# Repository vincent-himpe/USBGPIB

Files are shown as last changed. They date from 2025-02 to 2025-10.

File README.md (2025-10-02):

USBGPIB
=======

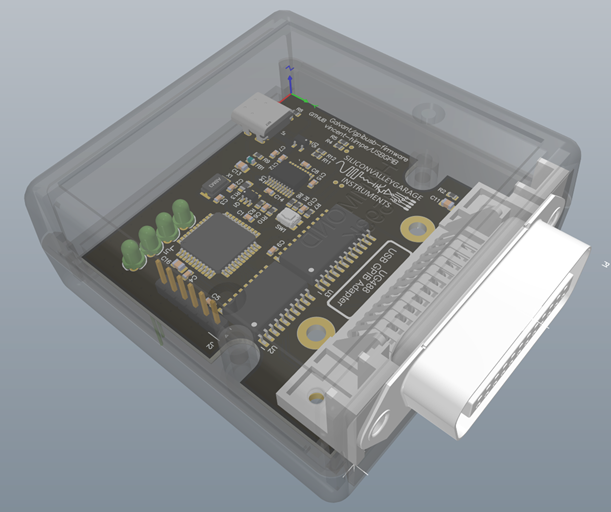
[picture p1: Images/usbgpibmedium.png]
mk-iii


This is a fork of the USB to GPIB adapter found at https://github.com/Galvant/gpibusb-pcb

See the following repos for more information

Firmware: https://www.github.com/Galvant/gpibusb-firmware

Docs: https://www.github.com/Galvant/gpibusb-documentation

Bootloader: https://www.github.com/Galvant/gpibusb-bootloader

This is only a HARDWARE fork ! The existing firmware/bootloadr/documentation will work on this board.

The original data is preserved in the REV4 folder.

## Changes

- Converted project to Altium Designer
- Changed the FTDI chip from a QFN package to SSO20 for easier soldering.
- Clean up schematic.
- Clean up all footprints and load 3D models
- Change board outline.
- Redone all routing.
- Change to 4 layer board.
- Designed the board to fit a small off-the-shelf Hammond enclosure.
- Endcap available as a PCB so you don;t have to drill the plastic endcap of the box.
- USB-C connector

## Layout

The Board is a 4 layer PCB that can easily be produced by the likes of JLCPCB or PCBway.  A full production pack (Gerber / NCdrill, BOM , Pick and place ) is available. 

## Assembly

The Bom and pick and place is included for assembly.

## Source Files

All source files are available in Altium Format. That's what i know, have and use. Other CAD programs most likely can import those. So you can modify.

## License

This work is released under the Creative Commons Attribution-Sharealike 3.0 license.
See http://creativecommons.org/licenses/by-sa/3.0/ or the included license/LICENSE.TXT file for more information.

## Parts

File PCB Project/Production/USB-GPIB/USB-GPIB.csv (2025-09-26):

Description | Designator | Quantity | LCSC
CAPACITOR,CERAMIC,100nF,50V,X7R,0603 | C1, C4, C5, C6, C7, C8, C9, C10, C12, C14, C15 | 11 | C127833
CAPACITOR,CERAMIC,18pF,50V,C0G,0603 | C2, C3 | 2 | C2169518
CAPACITOR,CERAMIC,10nF,200V,X7R,0805,ESD | C11 | 1 | C36911368
CAPACITOR,CERAMIC,10uF,25V,X5R,0805 | C13, C16 | 2 | C3039694
LED,TH,GREEN,42mCd,3MM, CONN,GPIB,24P,RIGHT ANGLE,TH | D1, D2, D3, D4, P1 | 5
DIODE,TVS,DUAL,UNIDIRECTIONAL,USB | D5 | 1 | C22358704
FERRITE,1KZ@100MHz,0R2DC,0603 | FB1 | 1 | C160982
OSHW LOGO, [NoValue] | G***, J2 | 2
CONN,USB-C,16P,RA,TH,8.94X9.17 | J1 | 1 | C7095263
XSTR,PMOS,20V,5.97A,VISHAY,SI3443,SOT26 | Q1 | 1 | C727385
RESISTOR,10K,1%,100mW,0603 (1608) | R1, R3 | 2 | C98220
RESISTOR,4K7,1%,100mW,0603 (1608) | R2 | 1 | C99782
RESISTOR,1K,1%,100mW,0603 (1608) | R4, R5, R6, R7, R10 | 5 | C22548
RESISTOR,5K1,1%,100mW,0603 (1608) | R8, R9 | 2 | C105580
RESISTOR,27R,1%,100mW,0603 (1608) | R11, R12 | 2 | C137753
RESISTOR,0R,JUMPER | R13 | 1 | C96345
SW,SMD,TACT,4PIN,2.9X3.5,4PIN | SW1 | 1 | C483888
IC,CPU,MICROCHIP,PIC18F4520,TQFP44 | U1 | 1 | C9734
IC,XCVR,GPIB,DATA.TI,SN75160DW,SO20W | U2 | 1 | C882412
IC,XCVR,GPIB,CONTROL,TI,SN75162DW,SO24W | U3 | 1 | C2863933
IC,XCVR,USB UART,FTDI,FT231XS-R,TSSOP20 | U4 | 1 | C132160
XTAL,18.432MHz,ABRACON ABM3,SMD5032 | X1 | 1 | C1985331

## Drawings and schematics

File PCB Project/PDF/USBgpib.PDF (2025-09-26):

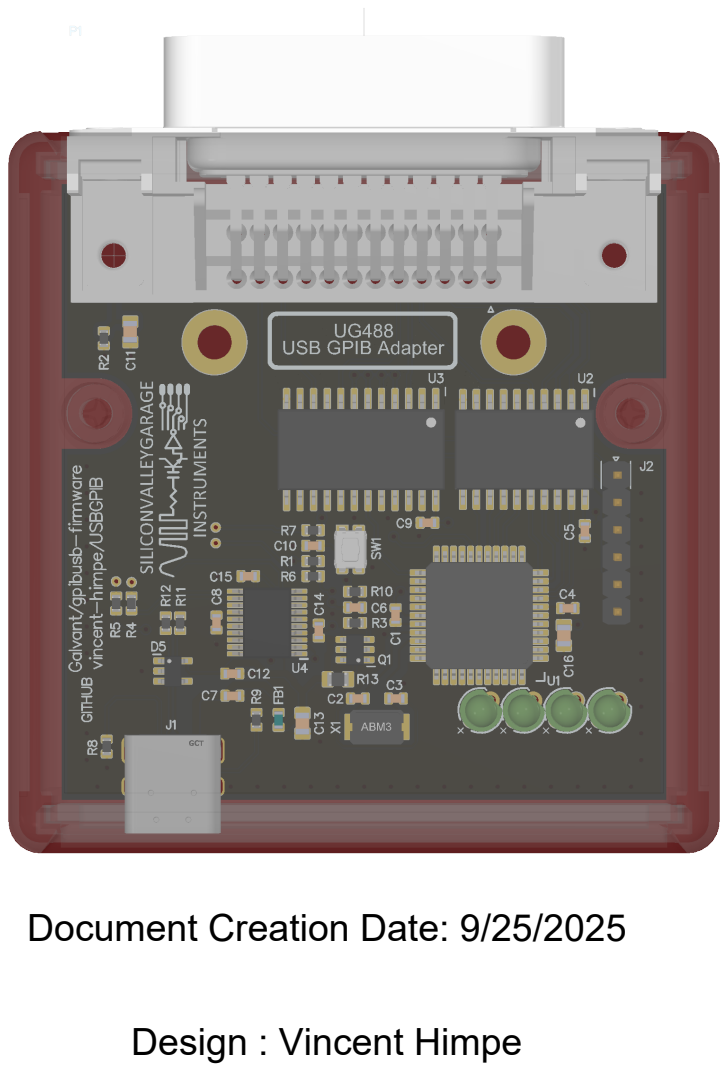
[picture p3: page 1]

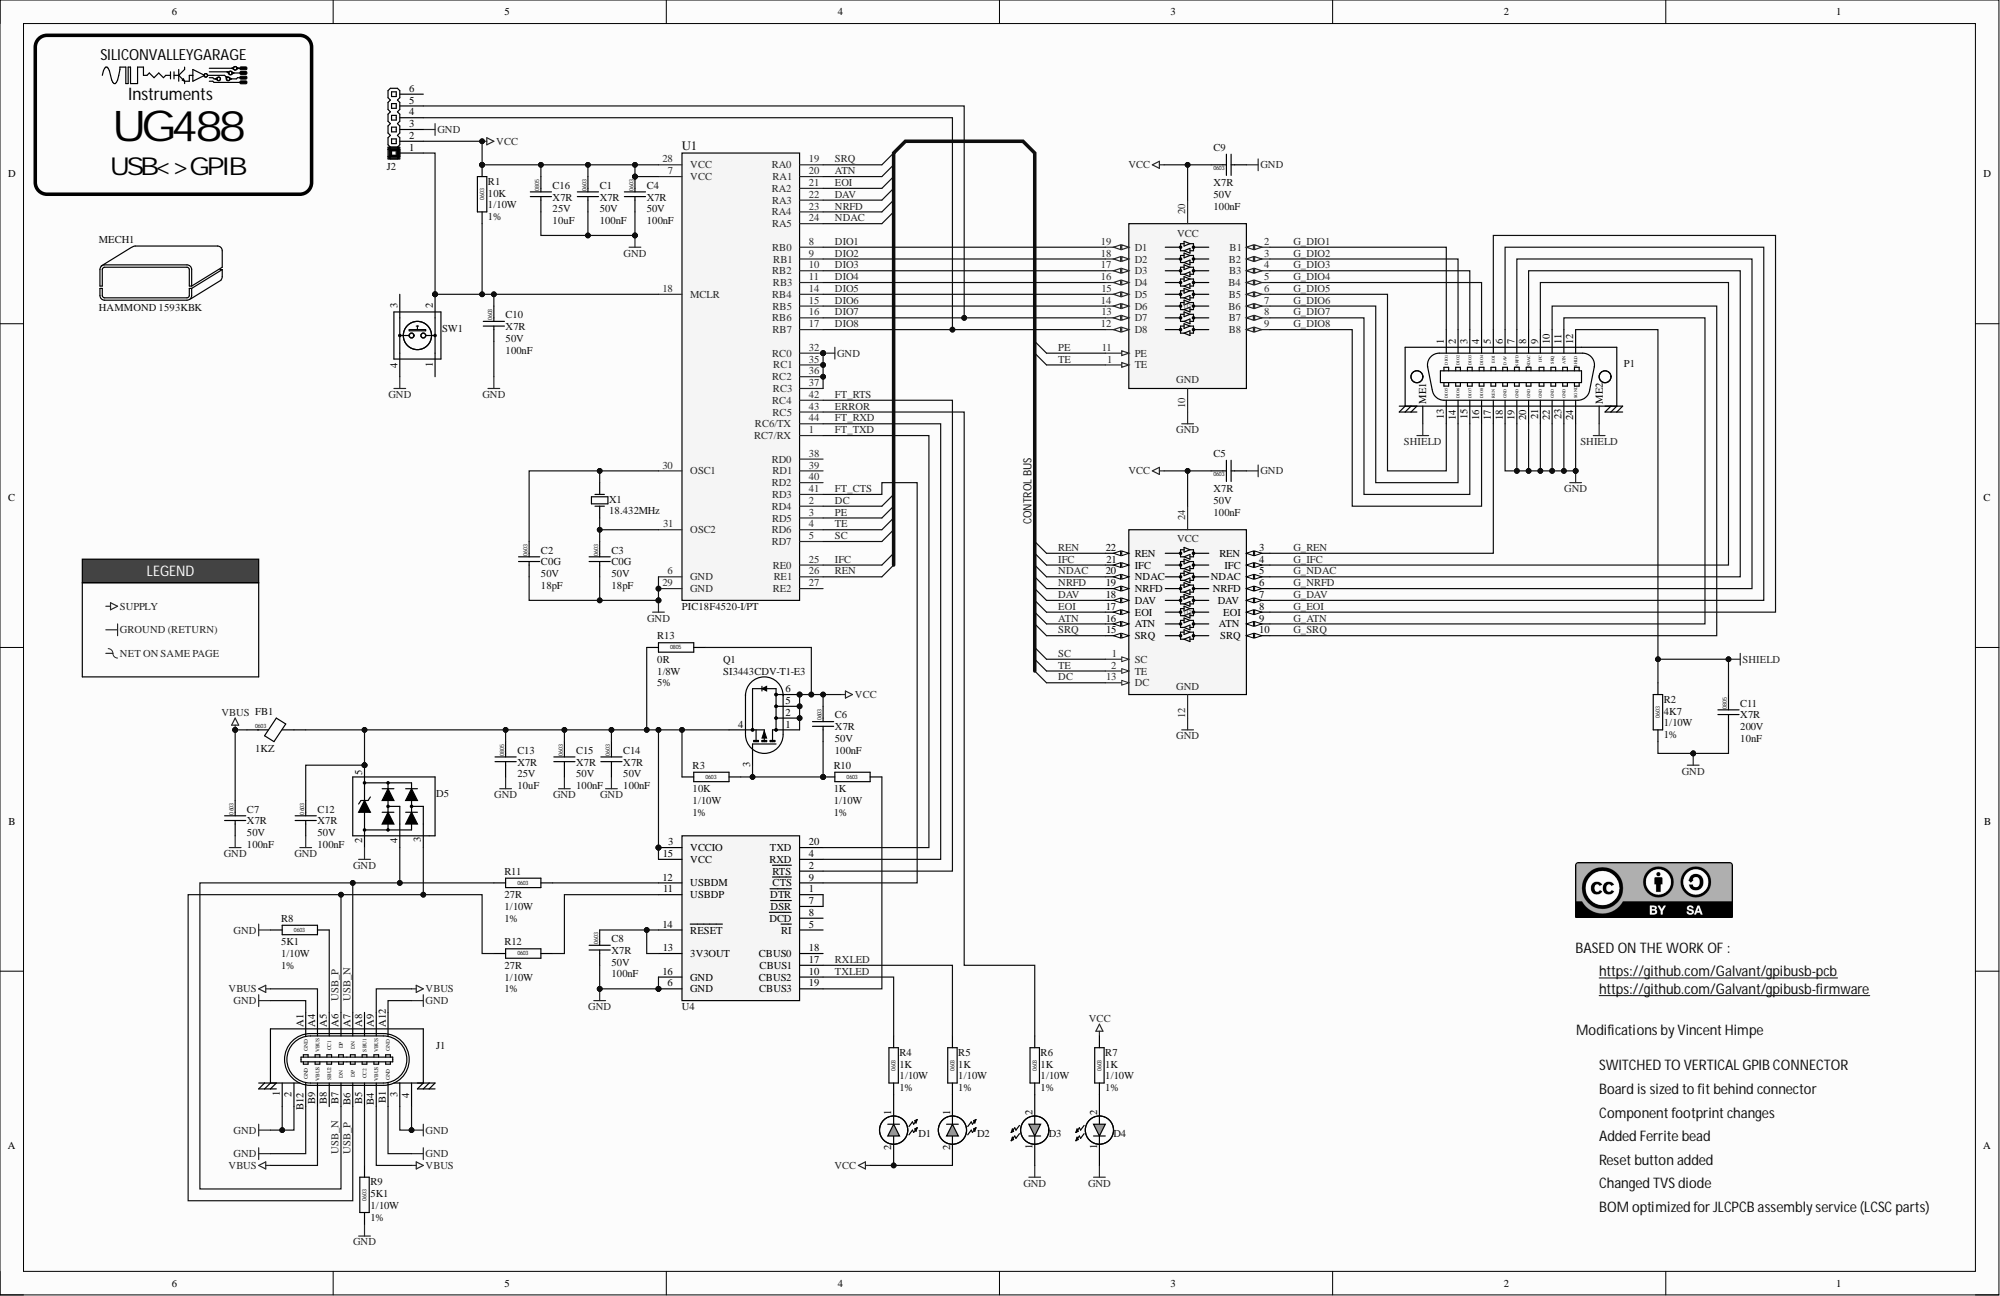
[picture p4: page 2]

SRQ ATN EOI DAV NRFD NDAC DC

1 0 DIO 3 | 1 7 | | 8 B6 7 B5 6 B4 5 B3 4 B2 3 B1 2 | G_ DIO 3
9 DIO 2 | 1 8 | | | G_ DIO 2

1 1 DIO 4 | 1 6 | | | G_ DIO 4
1 4 DIO 5 | 1 5 | | | G_ DIO 5

C1 0 | | 1 5 DIO 6 | | 1 4 | | G_ DIO 6

1 6 DIO 7 | 1 3 | | | G_ DIO 7
1 7 DIO 8 | 1 2 | | 9 | G_ DIO 8

RB7 RC0 RC1 RC2 RC3 RC4 RC5 RC6 /T X RC7 / RX RD 0 OSC 1 RD 1 RD 2 RD 3 RD 4 RD 5 OSC 2 RD 6 RD 7 RE 0 G N D RE 1 G N D RE 2

4 3 | ERRO R
4 4 | FT _ RX D

IFC
SRQ ATN EOI DAV NRFD NDAC

9 | G_ AT N
1 0 | G_SRQ

BASED ON THE WORK OF :

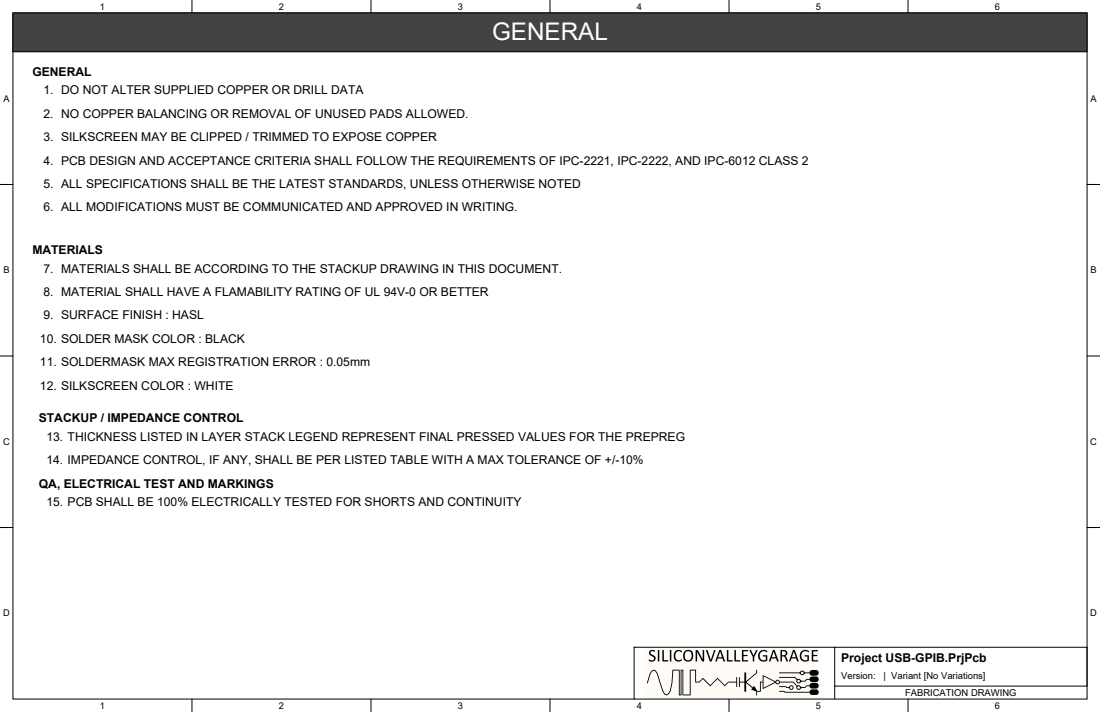
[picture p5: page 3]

GENERAL
1. DO NOT ALTER SUPPLIED COPPER OR DRILL DATA
2. NO COPPER BALANCING OR REMOVAL OF UNUSED PADS ALLOWED.
3. SILKSCREEN MAY BE CLIPPED / TRIMMED TO EXPOSE COPPER
4. PCB DESIGN AND ACCEPTANCE CRITERIA SHALL FOLLOW THE REQUIREMENTS OF IPC-2221, IPC-2222, AND IPC-6012 CLASS 2
5. ALL SPECIFICATIONS SHALL BE THE LATEST STANDARDS, UNLESS OTHERWISE NOTED
6. ALL MODIFICATIONS MUST BE COMMUNICATED AND APPROVED IN WRITING.

MATERIALS
7. MATERIALS SHALL BE ACCORDING TO THE STACKUP DRAWING IN THIS DOCUMENT.
8. MATERIAL SHALL HAVE A FLAMABILITY RATING OF UL 94V-0 OR BETTER
9. SURFACE FINISH : HASL
10. SOLDER MASK COLOR : BLACK
11. SOLDERMASK MAX REGISTRATION ERROR : 0.05mm
12. SILKSCREEN COLOR : WHITE

STACKUP / IMPEDANCE CONTROL
13. THICKNESS LISTED IN LAYER STACK LEGEND REPRESENT FINAL PRESSED VALUES FOR THE PREPREG
14. IMPEDANCE CONTROL, IF ANY, SHALL BE PER LISTED TABLE WITH A MAX TOLERANCE OF +/-10%
QA, ELECTRICAL TEST AND MARKINGS
15. PCB SHALL BE 100% ELECTRICALLY TESTED FOR SHORTS AND CONTINUITY

Project USB-GPIB.PrjPcb
Version: | Variant [No Variations]

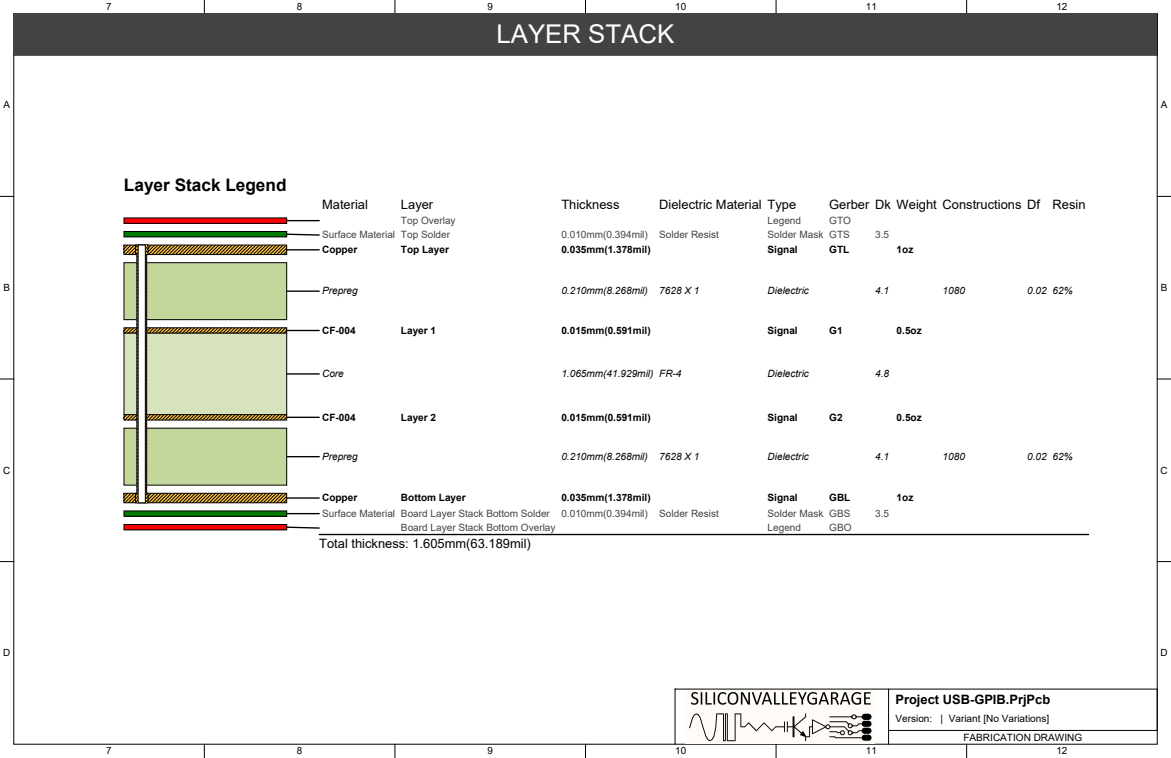
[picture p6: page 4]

Transmission Line Structure Table

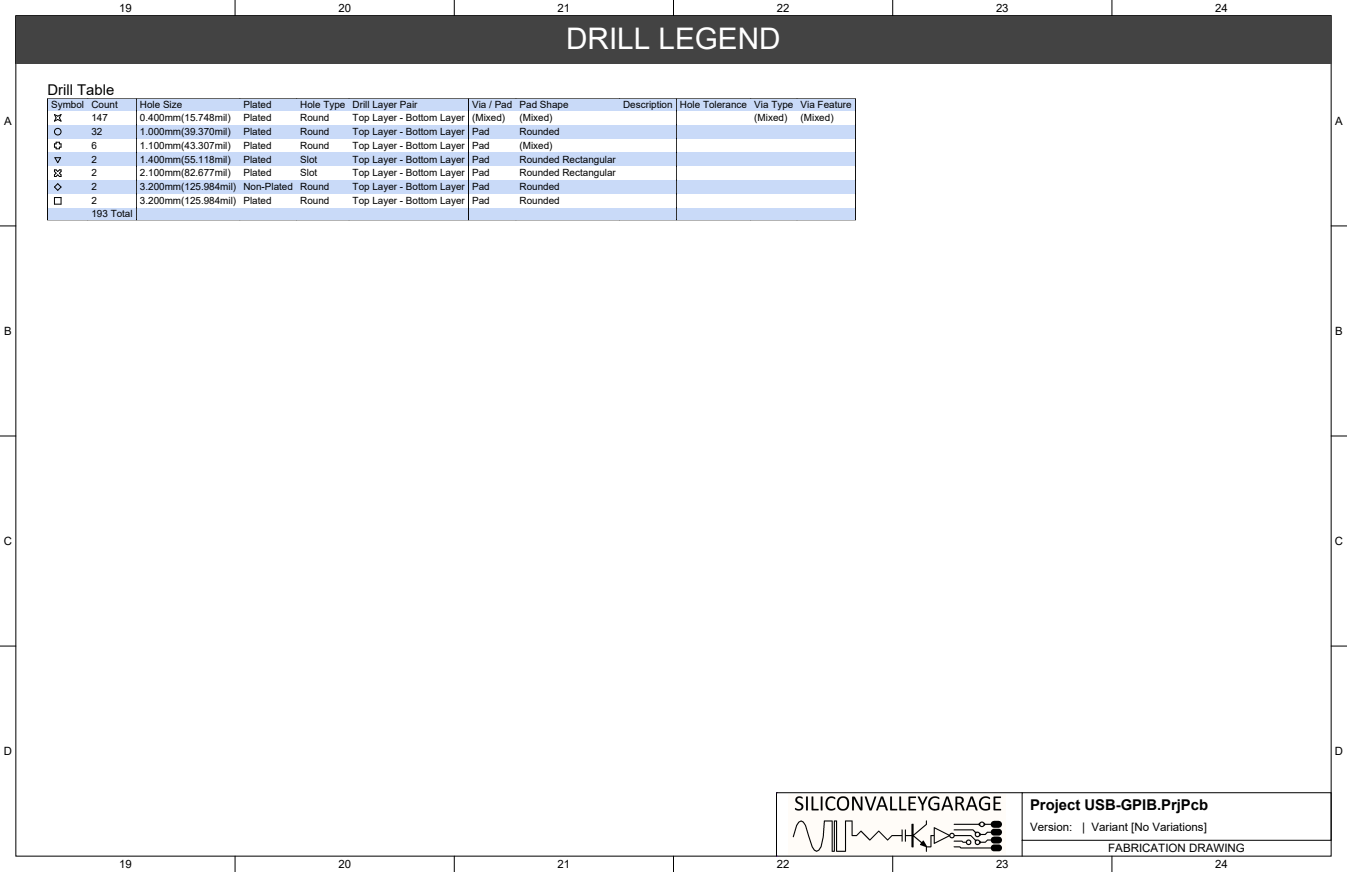
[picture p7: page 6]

Symbol | Count | Hole Size | Plated | Hole Type | Drill Layer Pair | Via / Pad | Pad Shape | Description | Hole Tolerance | Via Type | Via Feature

147 | 0.400mm(15.748mil) | Plated | Round | Top Layer - Bottom Layer | (Mixed) | (Mixed) | | | (Mixed) | (Mixed)
32 | 1.000mm(39.370mil) | Plated | Round | Top Layer - Bottom Layer | Pad | Rounded
6 | 1.100mm(43.307mil) | Plated | Round | Top Layer - Bottom Layer | Pad | (Mixed)
2 | 1.400mm(55.118mil) | Plated | Slot | Top Layer - Bottom Layer | Pad | Rounded Rectangular
2 | 2.100mm(82.677mil) | Plated | Slot | Top Layer - Bottom Layer | Pad | Rounded Rectangular
2 | 3.200mm(125.984mil) | Non-Plated | Round | Top Layer - Bottom Layer | Pad | Rounded
2 | 3.200mm(125.984mil) | Plated | Round | Top Layer - Bottom Layer | Pad | Rounded
193 Total

Drill Drawing View (Scale 3:1)

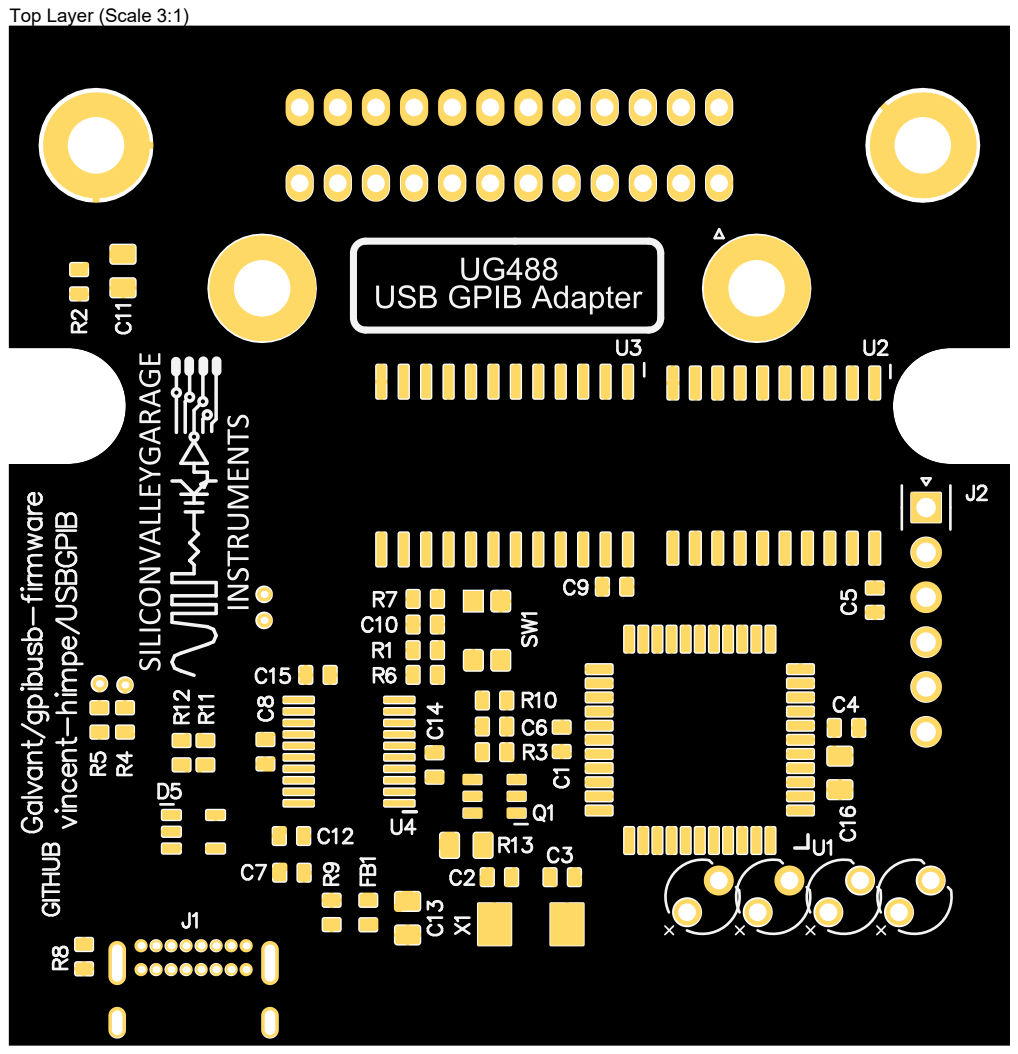
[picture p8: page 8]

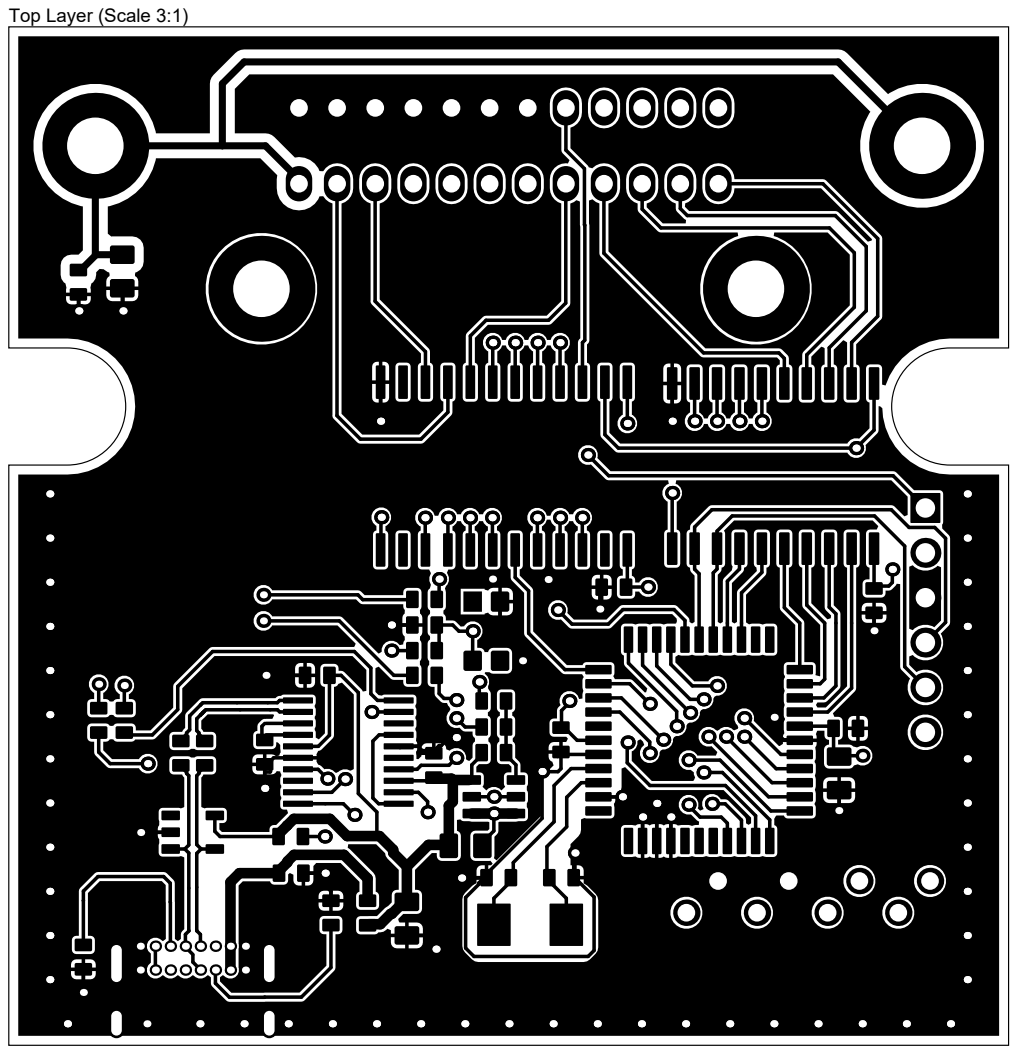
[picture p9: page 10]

LAYER VIEW : TOP LAYER

LAYER VIEW : MID LAYER 1

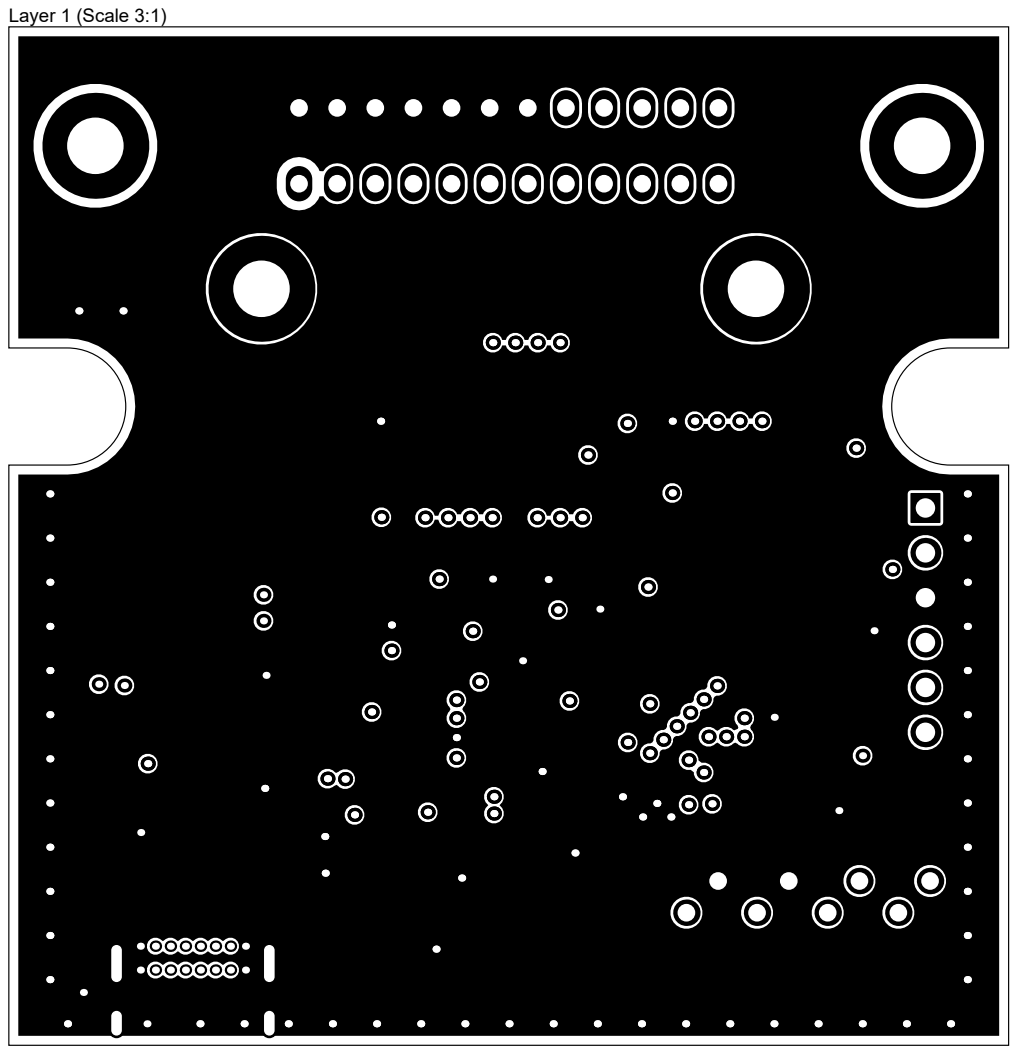
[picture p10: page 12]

LAYER VIEW : MID LAYER 2

LAYER VIEW : BOTTOM LAYER

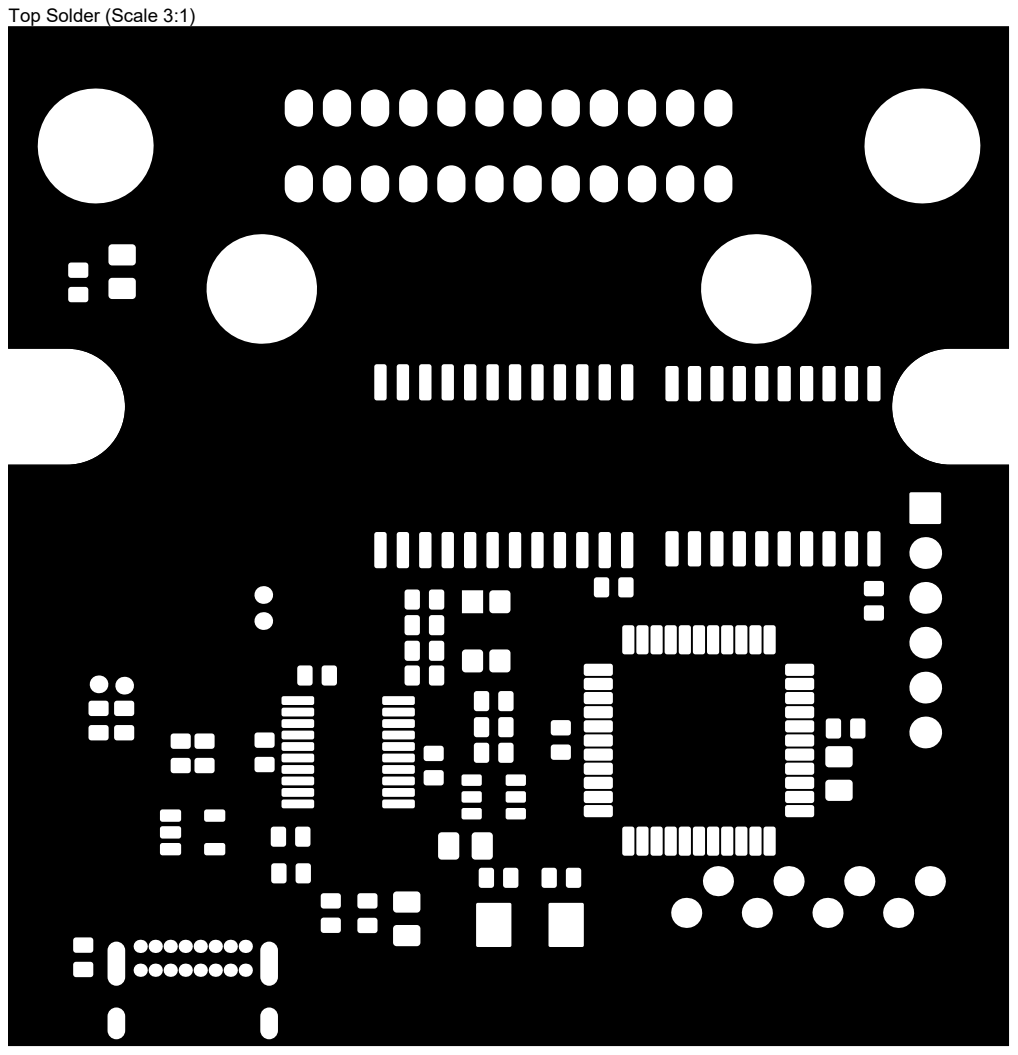
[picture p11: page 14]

LAYER VIEW : TOP SOLDER MASK

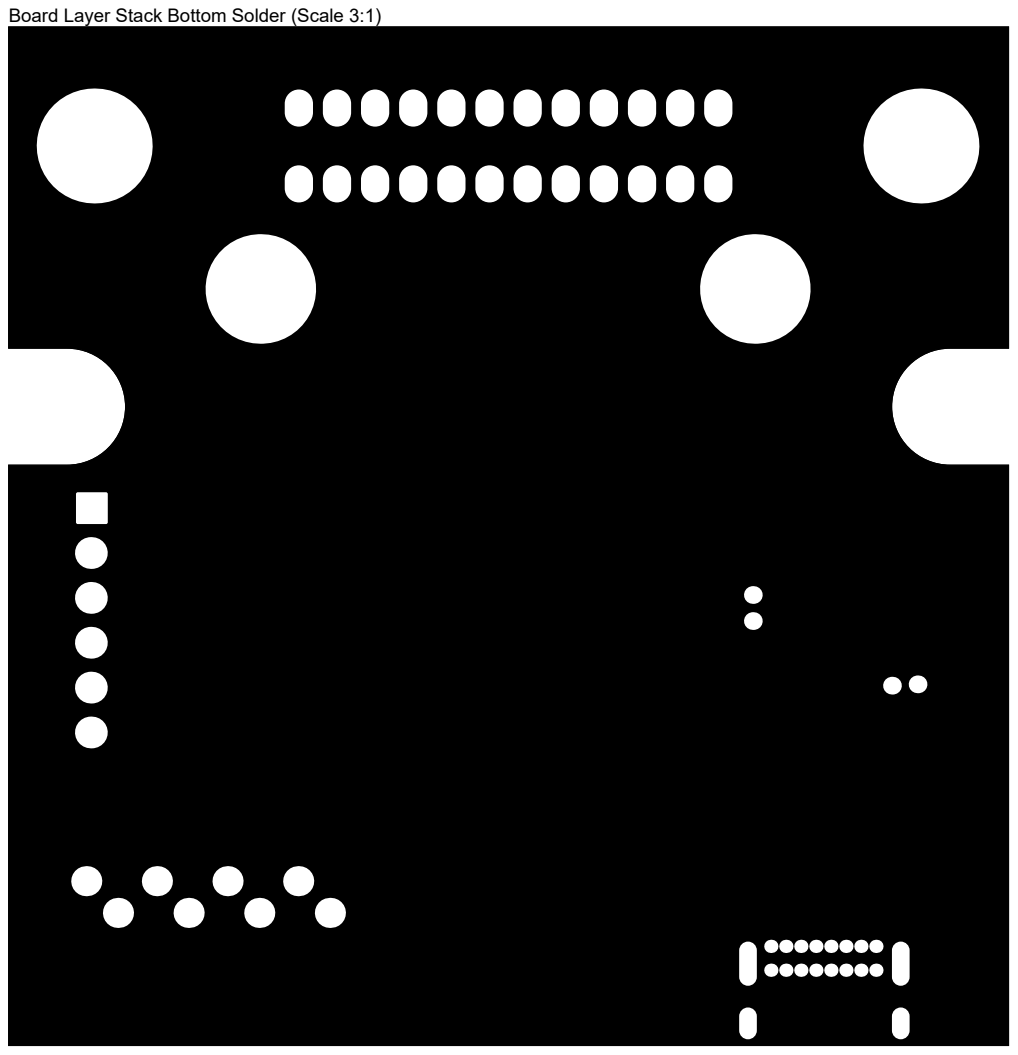
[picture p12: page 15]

LAYER VIEW : BOTTOM SOLDER MASK

Board Layer Stack Bottom Solder (Scale 3:1)

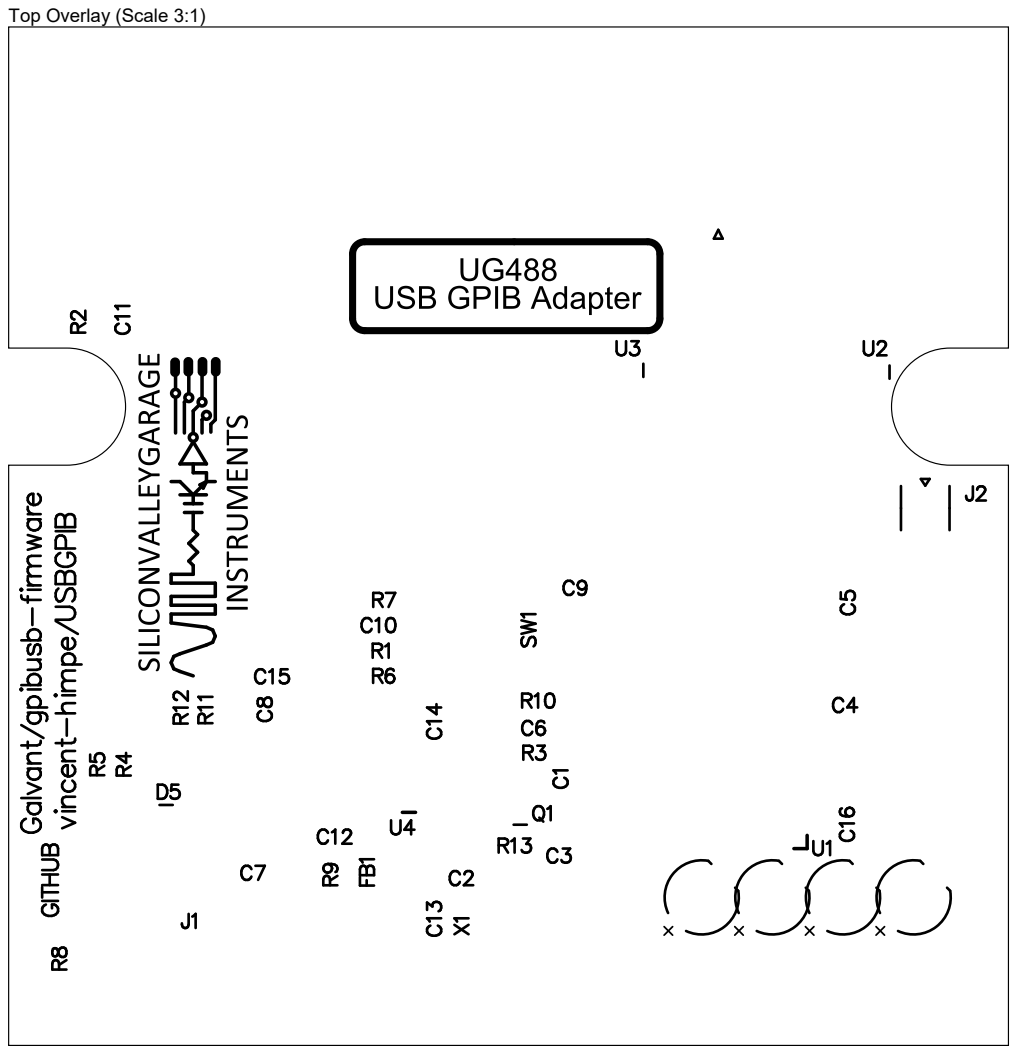
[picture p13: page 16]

LAYER VIEW : TOP SILKSCREEN (LEGEND)

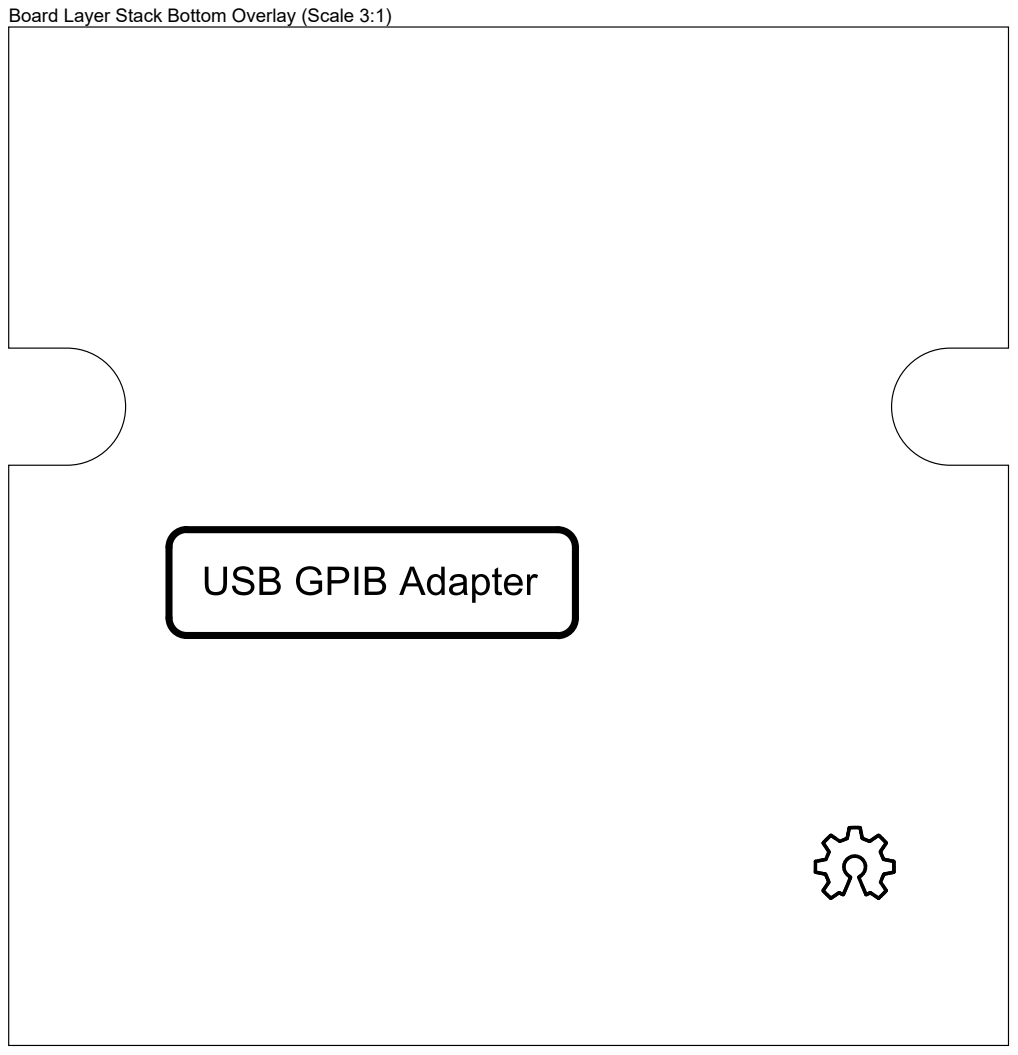
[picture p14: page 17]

LAYER VIEW : BOTTOM SILKSCREEN (LEGEND)

Board Layer Stack Bottom Overlay (Scale 3:1)


Unless otherwise specified the following rules apply:
1. DO NOT DEVIATE FROM ARTWORK OR BOM WITHOUT PRIOR AUTHORIZATION.
2. ASSEMBLE AND INSPECT PER IPC-610 CLASS 2

Bill of Materials and Material Handling
3. THE BOM CONTAINED IN THIS DOCUMENT IS AS-BUILT. NON-INSTALLED PARTS HAVE BEEN REMOVED. ADDITIONAL BOM FORMATS ARE AVAILABLE IN THE PROJECT FILES
4. ANY PART SUBSTITUTIONS MUST BE APPROVED IN WRITING BEFORE ASSEMBLY
5. ALL MATERIALS MUST BE PROCURED FROM MANUFACTURER AUTHORIZED DISTRIBUTORS OR THE ORIGINAL MANUFACTURER
6. ALL COMPONENTS AND BOARDS TO BE HANDLED AND STORED ACCORDING TO IPC GUIDELINES
7. ESD CONTROL PER IPC RULES

Soldering
8. SOLDERING TO BE DONE USING SN37PB63 ALLOY USING ALLOY MANUFACTURER RECOMMENDED NO-CLEAN FLUX
9. BGA COMPONENTS WITH LEAD-FREE CONNECTIONS NEED TO BE REBALLED WITH SN63PB37. MIXING OF ALLOYS IS NOT PERMITTED.
10. SOLDERING PREFERRABLY TO BE DONE USING NITROGEN ATMOSPHERE
11. SURPLUS COMPONENTS TO VACUUM SEALED WITH DESSICANT IN ANTISTATIC BAGS
12. INCOMING MATERIAL (BOARDS AND COMPONENTS) NEEDS TO BE INSPECTED FOR HUMIDITY AND BAKED IF NEEDED PRIOR TO USE.
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

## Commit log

2025-02-16 Archive Version 4
    Archive Version 4
    [usb_to_gpib-B_Cu.gbl, usb_to_gpib-B_Mask.gbs, usb_to_gpib-B_SilkS.gbo, usb_to_gpib-Edge_Cuts.gbr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]
2025-02-17 PCB Projectg commit
    [USB-GPIB.PrjPcb, USB-GPIB.SchDoc]
2025-02-18 layout mods
    [USB-GPIB.PrjPcb, USB-GPIB.SchDoc]
2025-07-02 CLEANUP START
    [USB-GPIB.PrjPcb, USB-GPIB.SchDoc]
2025-07-02 BOM WORK
    [USB-GPIB.SchDoc]
